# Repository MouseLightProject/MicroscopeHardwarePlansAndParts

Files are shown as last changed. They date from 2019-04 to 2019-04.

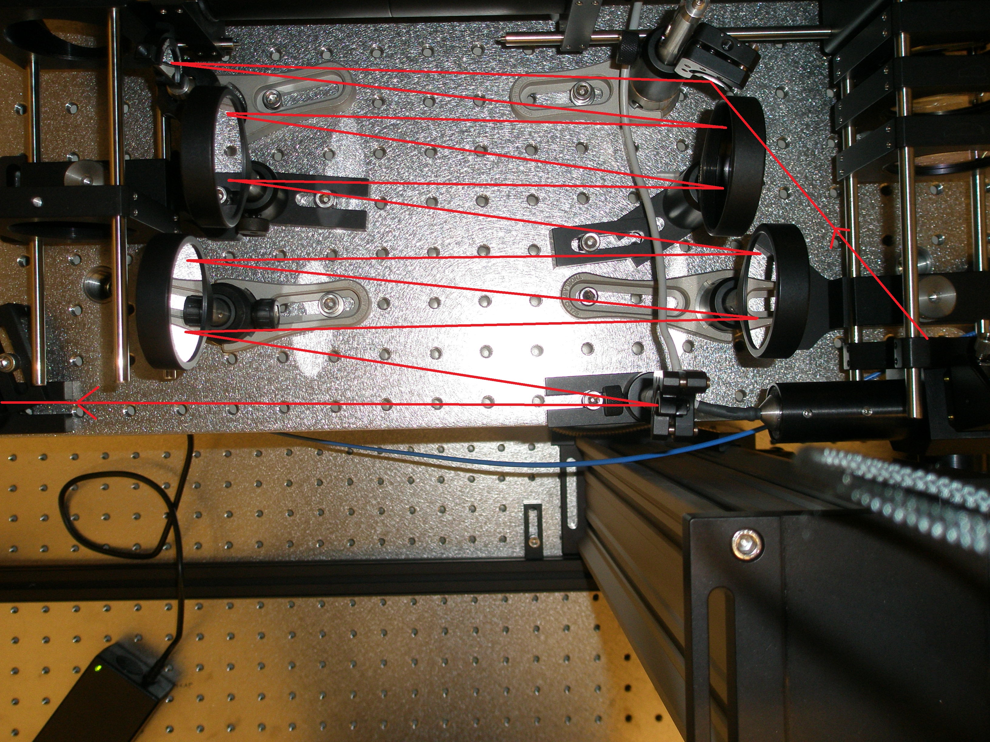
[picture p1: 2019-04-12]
Pictures/MouseBrainMicroscope_OpticalTriggerPic.JPG

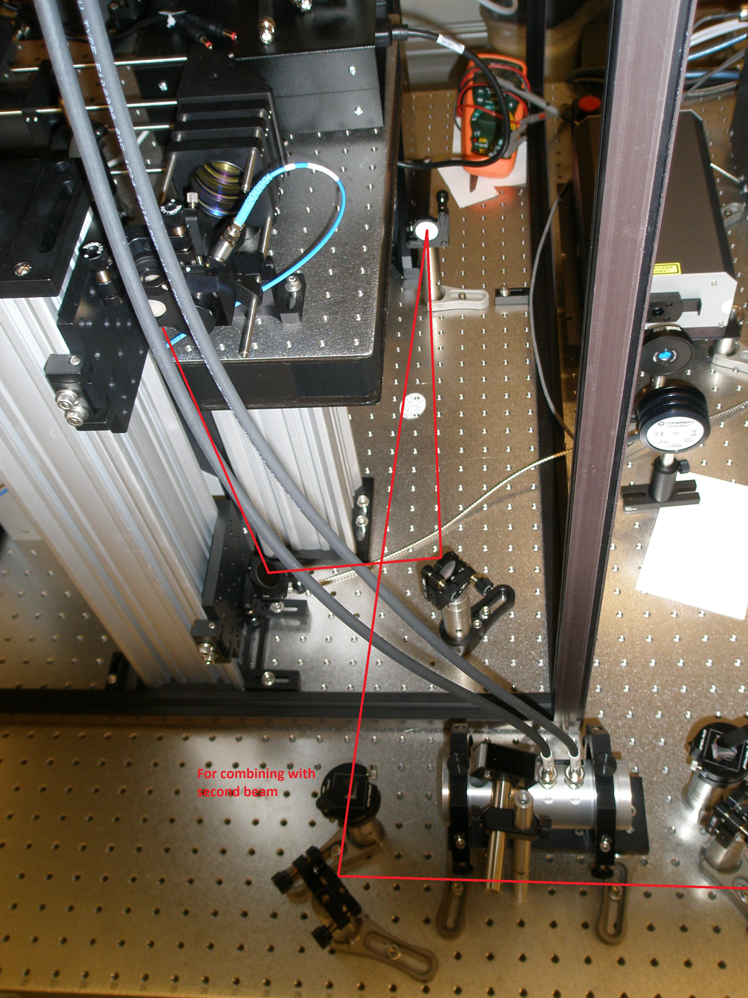
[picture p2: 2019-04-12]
Pictures/MouseBrainMicroscope_TableOpticsPic2.JPG

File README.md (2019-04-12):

# MouseLight Microscope Hardware

Hardware plans, component and assembly guide for the MouseLight microscope system described in [Economo et al., eLife, 2015](https://elifesciences.org/articles/10566)

## Contents
Please read the MouseLight_Microscope_AssemblyGuidelines for a rundown of the construction process and a table of content for the provided files and documentation.

## License
This project is licensed under the [Janelia Open-Source License](https://www.janelia.org/open-science/philosophy): see the LICENSE.md file for details

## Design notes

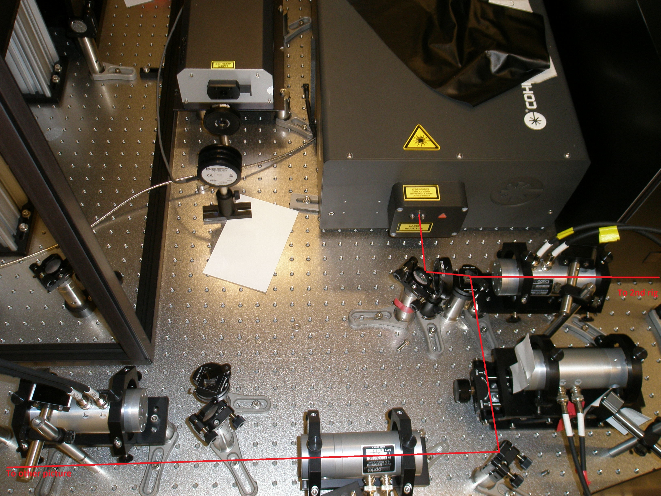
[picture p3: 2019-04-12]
Pictures/MouseBrainMicroscope_TableOpticsPic.JPG

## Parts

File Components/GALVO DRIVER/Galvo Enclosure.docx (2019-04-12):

Galvo Driver Enclsoure

Vault Folder: GALVOS

Nathan Clack

Research Specialist

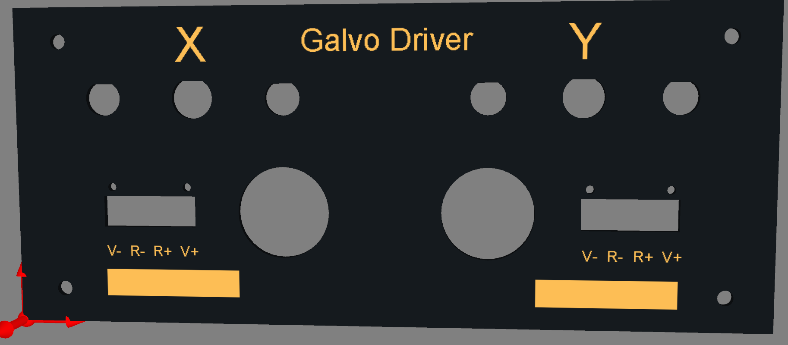
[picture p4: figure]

Steve Sawtelle
Electrical Engineer, ID&F
(571) 209-4158

# System Overview

The Galvo Driver Enclosure provides mounting, heat sink, and connectors for various Cambridge Technologies galvo drivers. One or two drivers can be mounted in the enclosure.

# Hardware Development

The Enclosure utilizes an off-the–shelf half-rack enclosure. The front panel can replaced by a custom front panel or the supplied panel can be modified to suit the particular need. The rear panel is replaced by a modular heat sink that provides various galvo mounting options. Wiring is highly dependent on the individual needs. The front panel design provides two BNCs and one Twin-Ax connectors for signal. A plug-able power supply connector is also provided for each channel. In addition a hole with grommet is provided for pass-through cables.

Materials

Qty | Value | Device | Manufacturer | Manufacturer PN | Digi-Key PN | Notes
1 | | Half-Rack Enclosure | Hammond | RMCV9038 | RMCV9038BK1-ND
1 | | Heat Sink | Aavid | 62725 | | Modified per drawing
1 | | Front Panel | Proto-Case | | | Custom design per drawing
2 | | Grommet | (McMaster-Carr) | 5269T65
2 | | BNC Male to Triax Female (3-Lug) | | | 1097-1008-ND | Adapt DAC output to Triac cable - shield isolated
4 | | BNC Bulkhead Jack, Panel Mount, Isolated | | | ACX1048-ND | For galvo monitor signals
2 | | Triax Jack, Bulkhead, 3 Lug | | | 501-1312-ND | For galvo command signals
2 | | 4 Position Terminal Block | | | 277-5751-ND | Panel mount for power
2 | | 4 Position Terminal Plug | | | 277-2432-ND | Wire to plug for power connector
AR | | Multiconductor Power Cable, 2 conductor, AWG 18, 250' spool | (Newark) | 62M3383 | | For power supply connection

# Assembly, Test, and Calibration

The galvo drivers should be lined up to the appropriate holes in the heat sink and attached with screws, with thermal grease between the heat sink and galvos.

The galvo drivers are wired up as required by the particular application.

Confidential Galvo Driver Enclosure

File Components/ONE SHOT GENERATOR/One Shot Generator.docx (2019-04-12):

One Shot Generator

Vault Folder: One-Shot Generator

Nathan Clack

Visiting Scientist

Magnus Karlsson
ID&F

# System Overview

This circuit creates an output pulse that happens exactly at the half-point of the input pulse with the possibility of some fine tuning using push-buttons. This eliminates manually setting a delay.

# Hardware Development

The circuit is made up of three parts:
1) An input detector (a comparator that compares the input to 3.3V/2)
2) An FPGA that
a) measures T = the length of time the output of the comparator is high (in units of 5 nS)
b) generates an output pulse T/2 ns after the output of the comparator goes high
3) Two push-buttons that allows an adjustment to the T/2 delay (in steps of +/- 5 nS) of the output

Schematic, Printed Circuit Board, BOM

See project file.

# Assembly, Test, and Calibration

No special requirements or notes.

Confidential One Shot Generator

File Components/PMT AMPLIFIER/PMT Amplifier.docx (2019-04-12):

PMT Amplifier

Karel Svoboda
Group Leader

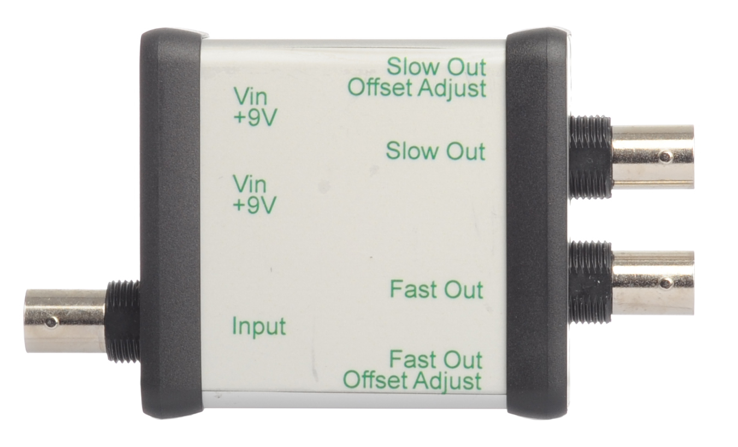
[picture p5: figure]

3/27/2012

Samantha Watkins
Engineering Specialist, ID&F
(571) 209-4371

# System Overview

The PMT Amplifier will be used as an error detector with microscope use. There will be fast and slow output. The fast output is the input signal from the PMT, but amplified with some filtering. The slow output will take the fast output and apply a low-pass filter with a 1 kHz roll off. The slow output will be an indicator of too long of a light exposure to the PMT, therefore the sensitive equipment, and will create a safety shutdown.

# Hardware Development

Materials

# Testing

The PMT Amplifier can be tested with a signal generator when RIN is replaced with a high value resistor. A PMT can also be used to test the Amplifier when a 0Ω resistor is used for RIN. The fast output should display a light pulse from the PMT and the slow output should give a low pass response when the PMT is exposed to too much light.

## Board Configurations

### R1: OPA657-OPA692-OP400

Stage 1: OPA657
Transimpedance Gain | 20 kΩ
Feedback Capacitor | 0.4 pF
Stage 2: OPA692
Gain | 2
Pulse Duration | 40 ns
Output Voltage Offset Adjust | Disabled. Pin grounded to allow for int. gain of 2
Stage 3: OP400
Gain | 1
Filter Cutoff – Freq Response | 1.6 kHz
Output Voltage Offset Adjust | Enabled

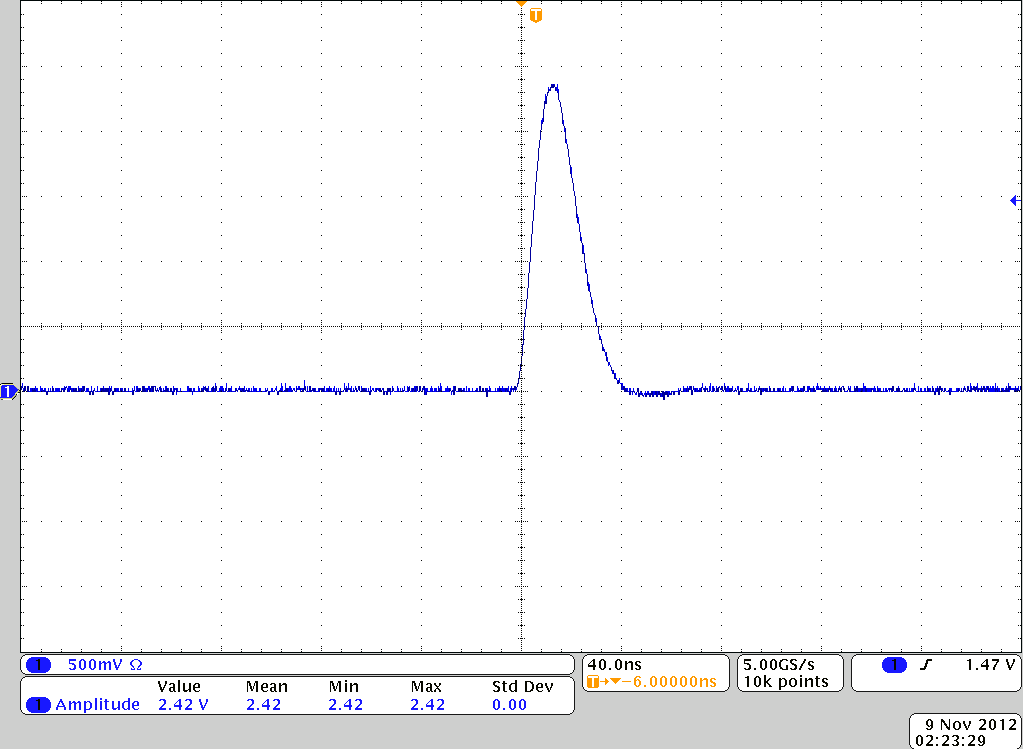
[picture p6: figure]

Fast Output from Stage 2: OPA657-OPA692-OP400

### R1: OPA657-AD810-OP400

Stage 1: OPA656
Transimpedance Gain | 100 kΩ
Feedback Capacitor | 0.5 pF
Stage 2: AD810
Gain | 2
Pulse Duration | 250 ns
Output Voltage Offset Adjust | Enabled
Stage 3: OP400
Gain | 1
Filter Cutoff – Freq Response | 1.6 kHz
Output Voltage Offset Adjust | Enabled

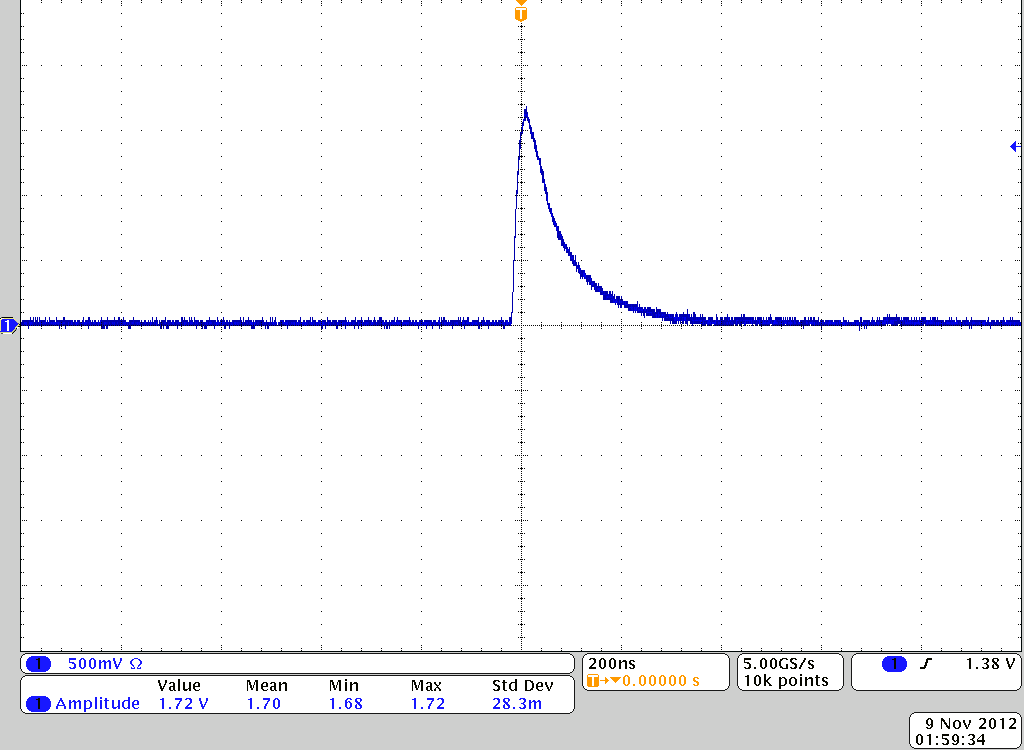
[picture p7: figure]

Fast Output from Stage 2: OPA657-AD810-OP400

### R1: OPA656-AD810-OP400

Stage 1: OPA656
Transimpedance Gain | 100 kΩ
Feedback Capacitor | 0.4 pF
Stage 2: AD810
Gain | 2
Pulse Duration | 180 ns
Output Voltage Offset Adjust | Enabled
Stage 3: OP400
Gain | 1
Filter Cutoff – Freq Response | 1.6 kHz
Output Voltage Offset Adjust | Enabled

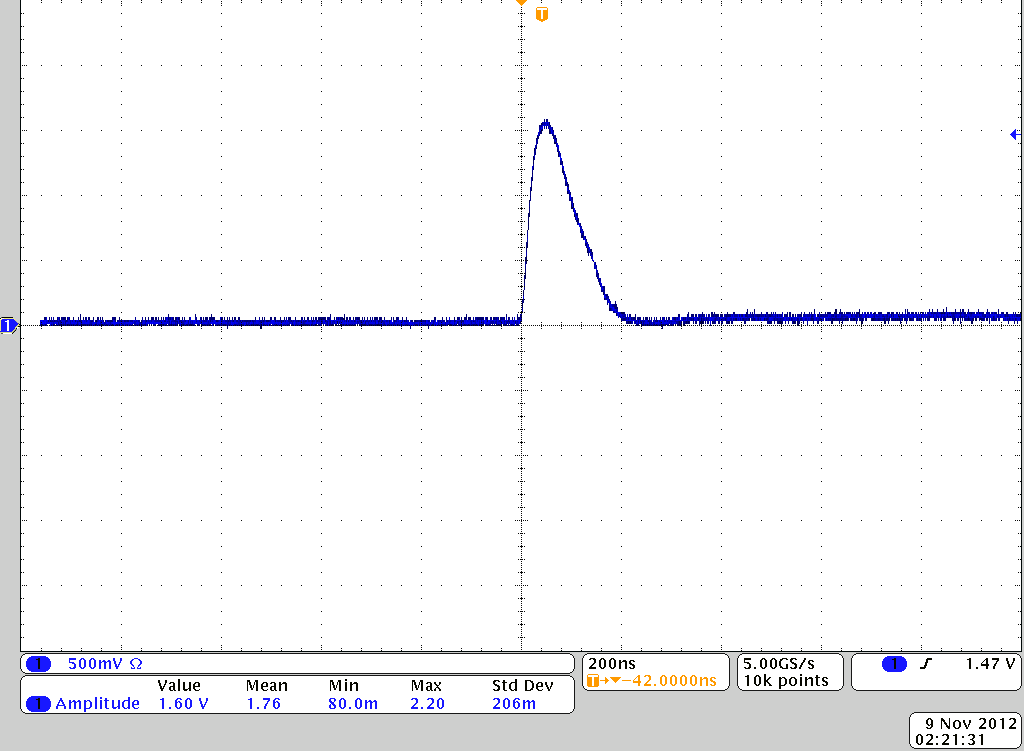
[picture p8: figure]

Fast Output from Stage 2: OPA656-AD810-OP400

### R1: OPA657-BUF634-OP400

Stage 1: OPA657
Transimpedance Gain | 100 kΩ
Feedback Capacitor | 0.4 pF
Stage 2: BUF634
Gain | 1
Pulse Duration | 320 ns
Output Voltage Offset Adjust | Disabled
Stage 3: OP400
Gain | 1
Filter Cutoff – Freq Response | 1.6 kHz
Output Voltage Offset Adjust | Disabled

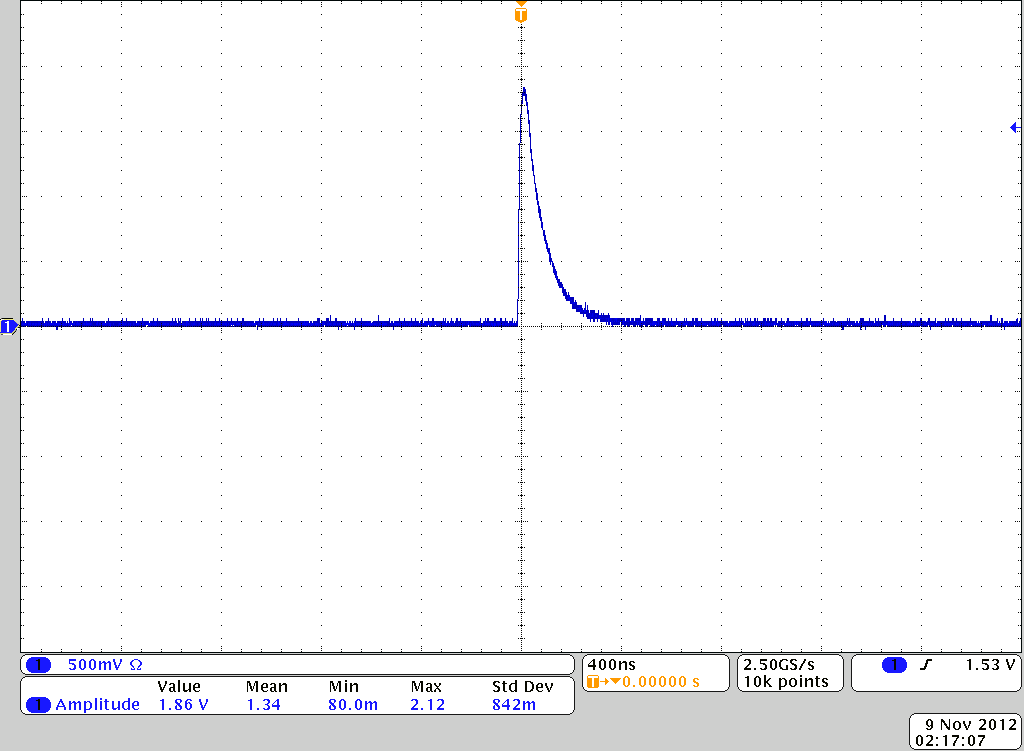
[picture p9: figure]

Fast Output from Stage 2: OPA657-BUF634-OP400

## Frequency and Gain Analysis

Freqin (@1V,20kΩ) | | Gain
| | OPA657 OPA692 | OPA657 AD810 | OPA656 AD810 | OPA657 BUF634
50kHz | 5.00E+04 | 7.4 | 5.72 | 5.76 | 6.4
100kHz | 1.00E+05 | 7.4 | 5.72 | 5.76 | 6.4
250kHz | 2.50E+05 | 7.4 | 5.72 | 5.76 | 6.4
500kHz | 5.00E+05 | 7.4 | 5.72 | 5.76 | 6.36
1MHz | 1.00E+06 | 7.36 | 5.56 | 5.64 | 6.36
2MHz | 2.00E+06 | 7.4 | 5.56 | 5.64 | 6.36
5MHz | 5.00E+06 | 7.4 | 5.2 | 5.32 | 6.36
10MHz | 1.00E+07 | 7.4 | 4.84 | 5 | 5.08
25MHz | 2.50E+07 | 7.2 | 3.32 | 3.64 | 2.2
50MHz | 5.00E+07 | 7.2 | 1.28 | 1.72 | 0.044
70MHz | 7.00E+07 | 6.8 | | 1.24 | 0.056
80MHz | 8.00E+07 | 6.4 | | 1
85MHz | 8.50E+07 | 6.1
90MHz | 9.00E+07 | 5.3
95MHz | 9.50E+07 | 4.8
100MHz | 1.00E+08 | 4.4
105MHz | 1.05E+08 | 3.96
110MHz | 1.10E+08 | 3.72

# Sample Circuit Set-Up

### R1: OPA656-AD810-OP400

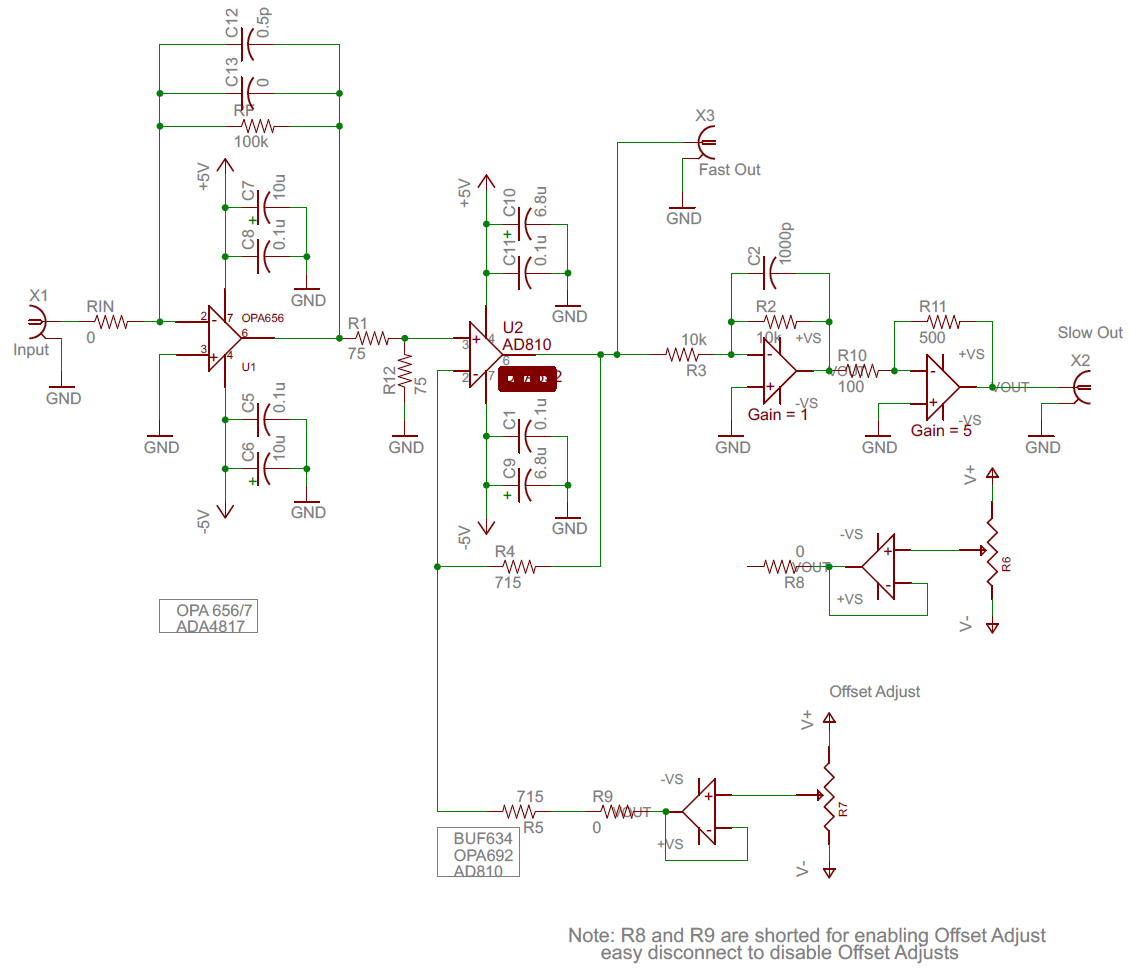
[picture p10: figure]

### R1: OPA657-BUF634-OP400

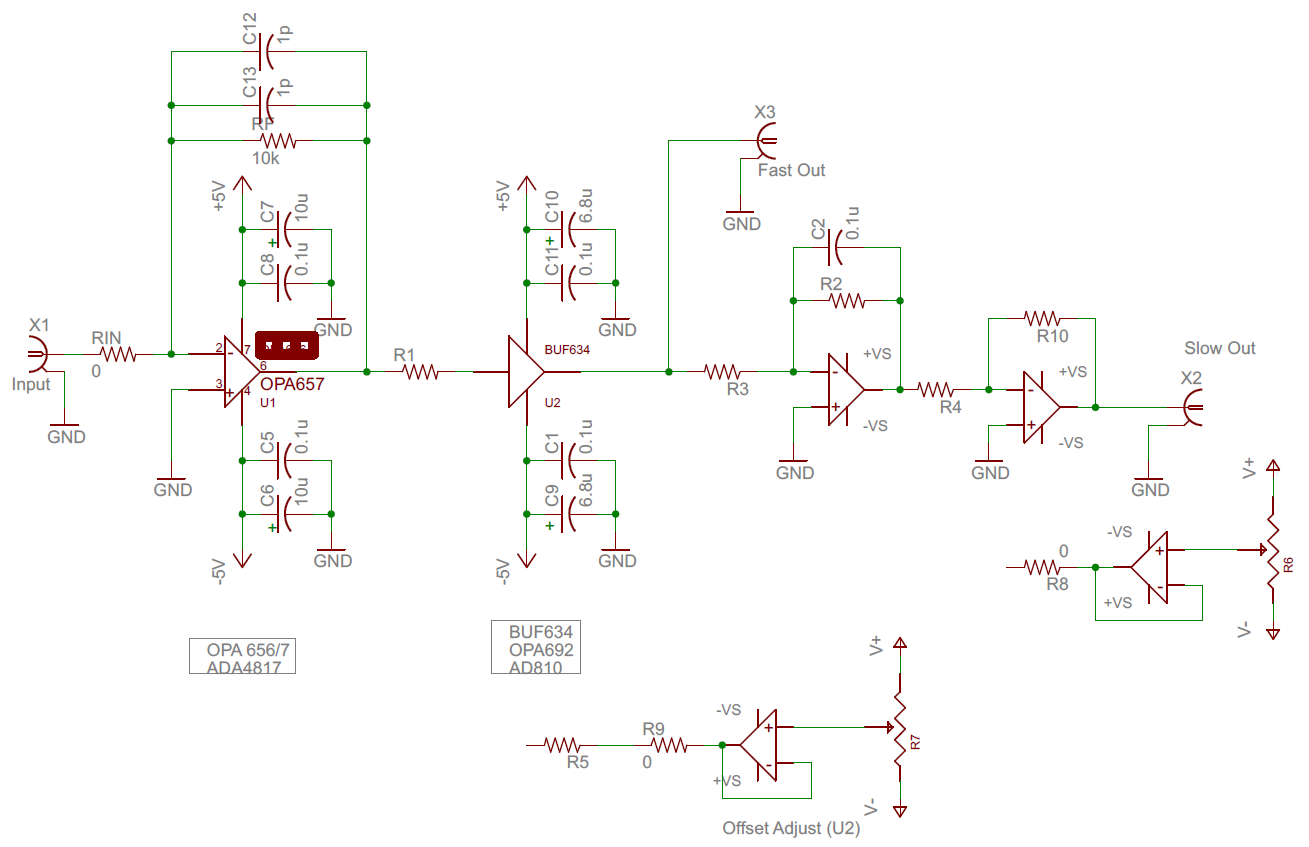
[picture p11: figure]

# Appendix

Assembly Note: R1 and Amp1 marked on the boards are the same, only differing in physical changes. Amp1 is the latest rendition in Vault as Revision B.


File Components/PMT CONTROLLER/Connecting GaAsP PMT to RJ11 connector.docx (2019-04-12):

Connecting GaAsP PMT to RJ11 connector.

The Hamamatsu H7422P-40MOD or H10770PB-40 SEL GaAsP PMTs terminate with bare wires. Connect the 4 power and control wires to a 4-6 (6 positions, 4 connectors, aka “RJ11”) modular plug a short distance from PMT. Attach a short piece of the appropriate 4 conductor cable to the connector with a crimper first, and then solder wires to wires.

Pinout:

PMT wire | PMT wire color | Connector pin
Vcc, +15V | Red | 4
GND | Black | 3
Vref | Blue | 2
Vcontrol | white | 1

Modular 6-4 (RJ11) connector pin assignment.


Pin 1

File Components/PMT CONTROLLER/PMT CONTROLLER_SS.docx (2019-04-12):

PMT CONTROLLER


The PMT Controller provides two channels of control for GaAsP Photo Multiplier Tubes. The low –noise design uses static logic, linear power supplies, and an AC line filters. The control voltages are independently adjustable over their entire range via a multi-turn control, with the voltages displayed on the built-in meters. Each PMT can be switched on and off independently. A trip circuit is built in to detect high PMT currents. Trip level and duration can be independently set for each channel. A trip condition turns off both PMTs and can be reset via a front panel control. External control of high voltage and trip reset are also provided.


Front Panel

- Trip Reset: resets a tripped condition
- LEDs: Power On, High Voltage On, Tripped
- Vctrl: Control Voltage Setting (each channel)
- PMT connector (each channel) Pin out (left to right):
  - 15V Supply Out
  - Ground
  - Reference Voltage In
  - Control Voltage Out
- PMT1 (2): Enable control for each PMT
- HV Ctl: High Voltage control: Normal or Override (Overrides trip)


Rear Panel

- AC inlet, power switch, fuse
- TTL HV CTL: External HV and trip control. Active high TTL, isolated) Pin out (left to right):
  - TTL Trip Reset In
  - TTL High Voltage Control In
  - Isolated Ground
  - 5V supply in for isolator
- PMT SIG: PMT pre-amp input for trip detect (each channel)
- Shield GND: Jumper to connect PMT SIG shield to local ground (each channel)
- Trip V: Adjust the trip detect level (monitor via test pin) (each channel)
- Trip Time: Adjust how long trip level must be active before trip (monitor via test pin) (each channel)
- GND: test point ground reference

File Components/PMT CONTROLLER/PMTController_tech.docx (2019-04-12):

PMT Controller

Vault Folder: PMT Controller

Nathan Clack

Research Specialist


Steve Sawtelle
Electrical Engineer, ID&F
(571) 209-4158

# System Overview

The PMT Controller provides two channels of control for GaAsP Photo Multiplier Tubes. The low –noise design uses static logic, linear power supplies, and an AC line filters. The control voltages are independently adjustable over their entire range via a multi-turn controls, with the voltages displayed on the built-in meters. Each PMT can be switched on and off independently. A trip circuit is built-in to detect high PMT currents. Trip level and duration can be independently set for each channel. A trip condition turns off both PMTs and can be reset via a front panel control. External control of high voltage and trip reset are also provided.

# Hardware Development

The PMT Controller is based off a previous Janelia design. Care was taken to eliminate switching noise. Only the panel meters use switching electronics.

The trip detect circuits have some high frequency noise filters (~30kHz), followed by a level comparator with adjustable threshold. This is followed by an adjustable trip delay circuit. Therefor a trip detect occurs when the input signal reaches a particular threshold and lasts a certain duration. The two trip signals are OR’ed together to create single trip event if either input satisfies the trip requirements. This in turn sets a latch to turn off the high voltage control and a trip indicator LED. The trip condition can be reset using the Trip Reset switch.

Each channel can be turned on and off independently. There is a common high voltage control.

Schematic


Printed Circuit Board


Materials

Qty | Value | Device | Manufacturer | Manuafcturer PN | Digi-Key PN | Designators
1 | 66010-004LF | RJ9 4P4C | FCI | 66010-004LF | 609-3785-ND | J1
2 | | HEADER 1X2 M RA | Molex | 22-12-2021 | WM2733-ND | JP1 JP2
1 | | HEADER 1X4 M ST | TE Connectivity | 3-644456-4 | A31114-ND | JP3
2 | | SWITCH-3PDT-VERT3PDT_VERT_RA | NKK | M2032S2A2W40 | 360-2858-ND | SW100 SW101
1 | | SWITCH-DPDT ON-NONE-ON | C&K | 7201P3CWAV2SE | CKN9728-ND | S1
1 | | SWITCH-SPDT ON-NONE-MOM | C&K | 7108P3CWAV2QE | CKN9716-ND | S100
5 | | TEST POINT | Keystone | 1045 | 1045K-ND | P1 P2 P3 P4 P5
11 | 0.1 | CAPS0805S | KEMET | C0805C104K1RACTU | 399-3486-1-ND | C5 C6 C7 C8 C12 C15 C16 C17 C18 C21 C22
2 | 0R-DNI | RESISTOR_SM0805S | DNI | DNI | DNI | R20 R21
2 | 5227161-9 | BNC, PCB , RA, LOW | TE Connectivity | 5227161-9 | A32261-ND | J2 J3
2 | 1K | RESISTOR_SM0805S | VISHAY | CRCW08051K00FKEA | 541-1.00KCCT-ND | R7 R9
2 | 1uF | CAPS0805S | Kemet | C0805C105KRACTU | 399-7409-1-ND | C3 C4
2 | 1uF/35V | CAPS0805S | MURATA | GRM31CR61H106KA12L | 490-5961-1-ND | C19 C20
8 | 2K | RESISTOR_SM0805S | VISHAY | CRCW08052K00FKEA | 541-2.00KCCT-ND | R5 R6 R16 R17 R18 R22 R26 R27
2 | 10K | POT3362M | Bourns | 3362M-1-103LF | 3362M-103LF-ND | R1 R4
4 | 10K | RESISTOR_SM0805S | VISHAY | CRCW080510K0FKEA | 541-10.0KCCT-ND | R11 R12 R13 R14
4 | 10uF/35V | CAPS1206S | TAIYO YUDEN | GMK316AB7106KL-TR | 587-3007-1-ND | C9 C10 C13 C14
2 | 16.9K | RESISTOR_SM0805S | VISHAY | CRCW080516K9FKEA | 541-16.9KCCT-ND | R23 R24
1 | 19E40 | ACOPIAN_PS | Acopian | 19E40 | from manufacturer | PS100
2 | 20K | POT3362M | Bourns | 3362M-1-203LF | 3362M-203LF-ND | R2 R3
3 | 20K | RESISTOR_SM0805S | VISHAY | CRCW080520K0FKEA | 541-20.0KCCT-ND | R15 R19 R25
1 | 47pF | CAPS0805S | JOHANSON | 500R15N470JV4T | 709-1175-1-ND | C11
2 | 50K | POT | Bourns | 3590P-4-503L | 3590P-4-503L-ND | R28 R29
1 | 74AHC1G02DBV | 74AHC1G02DBV | TI | SN74AHC1G02DBVR | 296-1088-1-nd | U3
1 | 74AHC1G08DBV | 74AHC1G08DBV | TI | SN74AHC1G08DBVR | 296-1091-1-ND | U8
2 | 100K | RESISTOR_SM0805S | VISHAY | CRCW0805100KFKEA | 541-100KCCT-ND | R8 R10
2 | 470pF | CAPS0805S - NPO | KEMET | C0805C471J5GACTU | 399-1133-2-ND | C1 C2
1 | 564-0200-132F | LED-TRI | DIALIGHT | 564-0200-132F | 350-1755-ND | D100
1 | 722RA | POWER_JACK_SHUNT | DNI | DNI | DNI | J4
1 | 74123D | IC MULTIVIBRATOR | NXP | 74HCT123D,653 | 568-9983-1-ND | U6
1 | 74279D | 74279D | TI | SN74LS279ADR | 296-29449-1-ND | U9
1 | ADG436 | ADG436 | ANALOG DEVICES | ADG436BRZ | ADG436BRZ | U10
1 | FOD0721 | OPTOCOUPLER | FAIRCHILD | FOD0721 | FOD0721-ND | U4
1 | 7019B-MTG | HEAT_SINK | AAVID | 7019B-MTG | 32-7019B-MT (MOUSER) | U$2
1 | LM340-5 | VREG_LM340_78X | TI | LM340T-5.0/NOPB | LM340T-5.0/NOPB-ND | U5
1 | LM340-15 | VREG_LM340_78X | TI | LM340T-15/NOPB | LM340T-15/NOPB-ND | U7
2 | FLEX CABLE/PCB | M12PTH | TE Connectivity | AFE12T/AF12/AFE12T | A9AAT-1202F-ND | JP4 JP5
2 | TLC3702 | COMPARATOR - DUAL | TI | TLC3702CDR | 296-1325-1-ND | U1 U2
1 | TS922 | OPAMP | ST MICRO | TS922IDT | 497-6035-1-ND | U11
2 | 5555979-1 | RJ11 6P4C | TE Connectivity | 5555979-1 | A31426-ND | J100 J101
2 | | HEADER-1X6-F | SAMTEC | SSQ-106-01-G-S | SAM1180-06-ND | ON DISPLAY BOARD
3 | | FERRITE- 0805-10uH | KEMET | L0805R100KPWST | 399-9588-1-ND | ON DISPLAY BOARD
1 | | DMM LED RED | MURATA | DMS-20PC-1-RS-C | 811-1001-ND | ON DISPLAY BOARD
1 | | DMM LED GRN | MURATA | DMS-20PC-1-GS-C | 811-1009-ND | ON DISPLAY BOARD
1 | | POWER ENTRY MODULE | DELTA | 06AR2D | 603-1132-ND | ON CHASSIS
3 | | CONN RECEPT FASTON 18-22AWG 250 | TE Connectivity | 696357-1 | 696357-1-ND | WIRED TO BOARD

# Assembly, Test, and Calibration

The PMT Controller is designed to require a minimum amount of wiring; most components mount directly to the main PCB.

PMT Controller Test Procedure

System Setup

1. PMT Controller
  a. Time trip potentiometer set to a minimum of 2ms
  b. Trip voltage potentiometer set to about 0.4V
    i. This can be measured using the test points; the center test point is ground
    ii. It can also be set by pointing the two dots on the potentiometer in the 9 o’clock position
    iii. This potentiometer ranges the trip voltage from about 0 - 4.6V
2. Pre-Amp – Stanford Research Systems SR570
  a. Make sure low noise is selected, 5µA/V, and invert are on/selected
  b. The filter, input offset, and bias voltage should all be off

Testing without the PMT

1. Using the 4 pin test cable check for noise in the power supply (J5, J6). Noise should be in the range of 5mV to 20mV peak to peak.
  a. This can be done by measuring between pins 1 and 2 of J5 and J6 with an AC Coupled channel.
2. The power supply for J5 and J6 should be at 15V.
3. Resistance across pins 2 and 3 of J5 and J6 should be 66kΩ with PMT Controller power turned off.
  a. It should not change when the potentiometer’s value is increased or decreased.

Testing with the PMT (p/n: ZD5760)


1. Make sure the PMT Controller is untripped before beginning the testing. Red LED should be off.
2. The LCD display should show a range from about 0 – 0.9V when the potentiometer is adjusted.
  a. This sets the gain for the PMT output pulse
3. Typically will not see anything on the oscilloscope with the gain less than 0.5V. Make sure the PMT pulse can be seen in the oscilloscope
4. Test trip by lowering the gain and blocking light from the PMT with your hand. Trip level should correspond with the trip voltage you set in the system setup section.

Confidential PMT Controller

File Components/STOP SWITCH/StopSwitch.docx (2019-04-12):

Stop Switch

Vault Folder: STOPSWITCH

Nathan Clack

Research Specialist


Steve Sawtelle
Electrical Engineer, ID&F
(571) 209-4158

# System Overview

The Stop Switch provides an emergency stop for stage drivers on a microscope. It consists of two parts: the stop switch in an enclosure and the interface electronics. The two are connected via a standard BNC cable.

# Hardware Development

The interface electronics is designed to be installed in-line with the existing cables so that no modifications are required.

The stop switch interface consists of OR’ing the stop line from each axis of the stage with the stop switch signal. The stop switch is a normally closed momentary switch. This ensures that any interruption, even a cut or missing cable will cause a STOP condition. Although any switch of this type can be used, a large prominent switch creates the best user interface.

Schematic


Printed Circuit Board


Materials

Partlist exported from C:/_Workspace/DATA/PROJECTS/STOPSWITCH/ECAD/StopSw_000333.sch at 8/29/2013 1:47:22 PM
| | | | Digi-Key | Manufacturer | Manufacturer PN
Qty | Value | Device | Designators
3 | | DB15 | J1 J2 J3 | A105027-ND | TE Connectivity | 3-106506-2
3 | | DB15DB15M | J4 J5 J6 | 5747841-6 | TE Connectivity | 5747841-6
4 | 0.1uF | CAPS0805S | C1 C2 C3 C4 | 478-3755-1-ND | AVX | 08053C104KAT2A
1 | 10K | RESISTOR_SM0805S | R1 | 541-10.0KCCT-ND | Vishay | CRCW080510K0FKEA
3 | 74AHC1G32DBV | 74AHC1G32DBV | IC1 IC2 IC3 | 296-1093-1-ND | TI | SN74AHC1G32DBVR
1 | 100 ohms | RESISTOR_SM0805S | R2 | 541-100CCT-ND | Vishay | CRCW0805100RFKEA
1 | BNC | 227161-9 | X1 | A32261-ND | TE Connectivity | 5227161-9
1 | | Enclosure (cut down) | | HM892-ND | Hammond | 1455J1601

STOP SWITCH - switch assembly
Quantity | Description | Manufacturer | PN | Source | Source PN | Notes
1 | Enclosure | Hammond | 1590AFLBK | Mouser | 546-1590AFLBK | Machine per picture
1 | Switch | | | McMaster | 5374T37
1 | BNC | Amphenol | 112624 | Mouser | 523-112624

# Assembly, Test, and Calibration


Wire the NC contact and common to the BNC connector.

Confidential Stop Switch

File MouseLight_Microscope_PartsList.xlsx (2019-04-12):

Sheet: BOM
Unit | Description | Part number | Rig qty | suggested spares | Qty to order | Item Cost | Rig cost | Rig unit subtotal | Spares cost | Spares Subtotal | Vendor | Old Quote # | Lead time | Comments | Inventor part file name | Column9 | Column10 | Column11 | Column12 | Column13 | Column14 | Column15 | Column16 | Column17 | Column18 | Column19 | Column20 | Column21 | Column22 | Column23 | Column24 | Column25 | Column26 | Column27 | Column28 | Column29 | Column30 | Column31 | Column32 | Column33 | Column34 | Column35 | Column36 | Column37 | Column38 | Column39 | Column40 | Column41 | Column42 | Column43 | Column44 | Column45 | Column46 | Column47 | Column48 | Column49 | Column50 | Column51 | Column52
Base and head movement | 2x1.5 ft custom size breadboard, research grade, with MicroLock | 04SI67446 | 1 | 0 | 1 | $1595 | $1595 | $2441.07 |  | $0 | Newport | 1054528 | 6 wk |  | Newport-04SI67446_Custom2x1p5ftBreadboard.ipt
Base and head movement | Elliptical mirror, 33 x 46.7 x 9.37mm, protected silver | 13E20ER.2 | 1 | 0 | 1 | $189 | $189 | $2441.07 |  | $0 | Newport |  |  |  | Newport_13E20ER.2_EllipSilverMirror.ipt
Base and head movement | Single Diameter Compression Tool for 1/32" Copper, Zinc-Plated Copper Sleeve | 3377T23 | 1 | 0 | 1 | $45.07 | $45.07 | $2441.07 |  | $0 | McMaster |  |  | Tool for fixing wire rope. Alternate methods of attaching head to cylinder are possible, but should be secure to avoid head dropping.
Base and head movement | Galvanized Steel Multipurpose Strand Rope, 1 x 7, 1/32" Diameter, 185 lb Break Strength, 50 ft. Length | 3498T41 | 1 | 0 | 1 | $1 | $1 | $2441.07 |  | $0 | McMaster |  |  | For attaching head to air cylinder
Base and head movement | Zinc-Plated Copper Oval Compression Sleeve for 1/32" Rope Diameter, 1/4" Sleeve Length, packs of 50 | 3898T29 | 1 | 0 | 1 | $1 | $1 | $2441.07 |  | $0 | McMaster |  |  | For attaching head to air cylinder
Base and head movement | Precision Thrd HI-Pressure Brass Pipe Fitting 1/8" Pipe Size, Tee, Fem X Male X Fem, 2900 PSI | 9171K860 | 1 | 0 | 1 | $16.73 | $16.73 | $2441.07 |  | $0 | McMaster-Carr |  |  |  | McMaster_9171K860_Tee.ipt
Base and head movement | Check valve, low cracking pressure, 1/8" NPT | AKB01B-N01S | 1 | 0 | 1 | $9.56 | $9.56 | $2441.07 |  | $0 | Allied Electronics/SMC | 1000238402 | 3 wk
Base and head movement | Metering valve w/ silencer, 1/8" NPT port | ASN2-N01-S | 1 | 0 | 1 | $4.24 | $4.24 | $2441.07 |  | $0 | Allied Electronics/SMC | 1000238402 | stock
Base and head movement | Aluminum shaft with DryLin S coating, OD 16mm, 254mm long. | AWM-16 | 2 | 0 | 2 | $14.86 | $29.72 | $2441.07 |  | $0 | IGUS | D475384REV0 | 1 wk |  | IGUS_16mmRod.ipt
Base and head movement | NC(D)G, High Speed/Precision Cylinder, Double Acting, Single Rod w/Options | NCGBN25-0500 | 1 | 0 | 1 | $28.86 | $28.86 | $2441.07 |  | $0 | Allied Electronics/SMC | 1000238402 | 3 wk |  | SMC_NCDGGN25-0500-U07US_Cylinder.iam
Base and head movement | Shock absorber, small | RBC0805 | 1 | 0 | 1 | $28.84 | $28.84 | $2441.07 |  | $0 | Allied Electronics/SMC | 1000238402 | 3 wk |  | SMC_RBC0805_ShockAbsorberSmall.ipt
Base and head movement | Pillow block, 16mm | RJUME-05-16 | 3 | 0 | 3 | $52.55 | $157.65 | $2441.07 |  | $0 | IGUS | D475384REV0 | 4-6 wk |  | IGUS_RJUME-05-16_PillowBlock16mm.iam
Base and head movement | 95mm structural rail, length .25 m | XT95-250 | 4 | 0 | 4 | $56.1 | $224.4 | $2441.07 |  | $0 | Thorlabs |  |  |  | Thor_XT95-250_95mmStructuralRail.ipt
Base and head movement | XT95 mounting plate | XT95P3 | 4 | 0 | 4 | $27.5 | $110 | $2441.07 |  | $0 | Thorlabs |  |  |  | Thor_XT95P3_XT95MountingPlate.ipt
Blocking slit hardware | Translating Post Holder, Min Height L1=2.38", Max Height L2=2.83" | PH2T | 1 | 0 | 1 | $54 | $54 | $146 |  | $0 | Thorlabs |  |  |  | PH2T_TranslatingPostHolderShort.iam
Blocking slit hardware | Center Mount 3" Post Joist | PJ301 | 3 | 0 | 3 | $16 | $48 | $146 |  | $0 | Thorlabs |  |  |  | PJ301_CenterMount3inPostJoist.ipt
Blocking slit hardware | Reaching 3" Post Joist | PJ302 | 1 | 0 | 1 | $15 | $15 | $146 |  | $0 | Thorlabs |  |  |  | PJ302_Reaching3inPostJoist.ipt
Blocking slit hardware | Universal post holder, height 1" | UPH1 | 1 | 0 | 1 | $29 | $29 | $146 |  | $0 | Thorlabs |  |  |  | Thor_UPH1_UnivPostHolder.ipt
Cage | Magnet tape | 5759K36 | 15 | 0 | 15 | $0.43 | $6.45 | $926.09 |  | $0 | McMaster-Carr |  |  | Feel free to use other, preferred methods for cage construction
Cage | Magnet tape, per foot, 1/16" thick, adhesive backed, strong pull | 5759K47 | 120 | 0 | 120 | $0.6 | $72 | $926.09 |  | $0 | McMaster-Carr |  |  | Feel free to use other, preferred methods for cage construction
Cage | Anodized Al sheet, 0.032 x 48.00 x 96.00 5005, Black anodize 2 stp class I | none | 2 | 0 | 2 | $110.72 | $221.44 | $926.09 |  | $0 | SAF.com |  |  | 4'x8' sheets need to be cut to size for cage with sheet metal shear. High freight charge is free for orders of 7 or more sheets
Cage | Construction cube | RM1G | 8 | 0 | 8 | $13.4 | $107.2 | $926.09 |  | $0 | Thorlabs |  |  | Feel free to use other, preferred methods for cage construction
Cage | Construction bracket | XE25A90 | 3 | 0 | 3 | $23.7 | $71.1 | $926.09 |  | $0 | Thorlabs |  |  | Feel free to use other, preferred methods for cage construction
Cage | Table clamp | XE25CL2 | 3 | 0 | 3 | $11 | $33 | $926.09 |  | $0 | Thorlabs |  |  | Feel free to use other, preferred methods for cage construction
Cage | Drop-In T-Nut, 1/4"-20 Tapped Hole, Qty: 10 | XE21T1 | 1 | 0 | 1 | $28 | $28 | $926.09 |  | $0 | Thorlabs |  |  | Feel free to use other, preferred methods for cage construction
Cage | 1/4"-20 Low-Profile Channel Screws (100 Screws/Box) | SH25LP38 | 1 | 0 | 1 | $21.6 | $21.6 | $926.09 |  | $0 | Thorlabs |  |  | Feel free to use other, preferred methods for cage construction
Cage | Construction rail, 30" long | XE25L30 | 4 | 0 | 4 | $24.5 | $98 | $926.09 |  | $0 | Thorlabs |  |  | Feel free to use other, preferred methods for cage construction
Cage | Construction rail, 36" long | XE25L36 | 3 | 0 | 3 | $27.5 | $82.5 | $926.09 |  | $0 | Thorlabs |  |  | Feel free to use other, preferred methods for cage construction
Cage | Construction rail, 48" long | XE25L48 | 4 | 0 | 4 | $34.7 | $138.8 | $926.09 |  | $0 | Thorlabs |  |  | Feel free to use other, preferred methods for cage construction
Cage | Blackout Fabric | BK5 | 1 | 0 | 1 | $46 | $46 | $926.09 |  | $0 | Thorlabs
Chromatic optics | IR stopping short pass filter | FF01-750/SP-30-D | 0 | 0 | 0 | $1200 | $0 | $1880 |  | $0 | Semrock |  | 1 Wk | Potentially helpful to stack with emission filters for IR blocking
Chromatic optics | Primary dichroic. | FF735-Di01-25x36 | 1 | 0 | 1 | $495 | $495 | $1880 |  | $0 | Semrock |  | 1 Wk
Chromatic optics | Secondary dichroic 35.5 x 50.2. Need to specify cutoff wavelength |  | 1 | 0 | 1 | $485 | $485 | $1880 |  | $0 | Semrock |  | 1 Wk | red/green secondary dichro. End user to specify filter coating. Need custom size: 35.5x50.2 mm. Easy to purchase custom size from Semrock.
Chromatic optics | Emission filter, channel 1, 30mm diam |  | 1 | 0 | 1 | $450 | $450 | $1880 |  | $0 | Semrock |  | 1 Wk | Emission filters need to have custom size 30mm diam. End user to specify filter coating. Easy to purchase custom size from Semrock. | EmissionFilter.ipt
Chromatic optics | Emission filter, channel 2, 30mm diam |  | 1 | 0 | 1 | $450 | $450 | $1880 |  | $0 | Semrock |  | 1 Wk | Emission filters need to have custom size 30mm diam. End user to specify filter coating. Easy to purchase custom size from Semrock.
Computer | Microsoft Visual Studio 2010 Professional w/MSDN | 2076506 | 1 | 0 | 1 | $591.51 | $591.51 | $4879.38 |  | $0 | CDW
Computer | Microsoft Windows 7 Professional SP1 64-bit | 2341134 | 1 | 0 | 1 | $141 | $141 | $4879.38 |  | $0 | CDW
Computer | Antec DF-85 Black Steel / Plastic ATX Full Tower Computer Case | N82E16811129087 | 1 | 0 | 1 | $139.99 | $139.99 | $4879.38 |  | $0 | Newegg |  |  | Exact match probably not necessary
Computer | StarTech Model TX3SPLIT12 12" TX3 Fan Power Splitter Cable | N82E16812200455 | 1 | 0 | 1 | $6.99 | $6.99 | $4879.38 |  | $0 | Newegg |  |  | Exact match probably not necessary
Computer | ASUS P9X79 WS LGA 2011 Intel X79 SATA 6Gb/s USB 3.0 SSI CEB Intel Motherboard with USB BIOS | N82E16813131798 | 1 | 0 | 1 | $379.99 | $379.99 | $4879.38 |  | $0 | Newegg |  |  | Exact match probably not necessary
Computer | EVGA 04G-P4-2690-KR GeForce GTX 690 4GB 512-bit GDDR5 PCI Express 3.0 x16 HDCP Ready SLI Support Video Card | N82E16814130781 | 1 | 0 | 1 | $999.99 | $999.99 | $4879.38 |  | $0 | Newegg |  |  | May not be available. Nvidia GTX 680 or better should be used.
Computer | StarTech PCI Express to 4 Slot PCI Expansion System Model PEX2PCI4 | N82E16815158247 | 0 | 0 | 0 | $426.99 | $0 | $4879.38 |  | $0 | Newegg |  |  | This part needed extensive mods to case to fit PI motor control cards. Probably best to order StarTech PEX2PCIE4L (listed separately), although this is untested
Computer | COOLER MASTER Silent Pro Gold Series RSC00-80GAD3-US 1200W ATX 12V v2.3 / EPS 12V v2.92 SLI Ready CrossFire Ready 80 PLUS GOLD Certified Modular Active PFC Power Supply | N82E16817171055 | 1 | 0 | 1 | $239.99 | $239.99 | $4879.38 |  | $0 | Newegg |  |  | Exact match probably not necessary
Computer | Intel Core i7-3930K Sandy Bridge-E 3.2GHz (3.8GHz Turbo) LGA 2011 130W Six-Core Desktop Processor BX80619i73930K | N82E16819116492 | 1 | 0 | 1 | $569.99 | $569.99 | $4879.38 |  | $0 | Newegg |  |  | Exact match probably not necessary
Computer | OCZ Vertex 4 VTX4-25SAT3-512G.M 2.5" 512GB SATA III MLC Internal Solid State Drive (SSD) | N82E16820227820 | 2 | 0 | 2 | $394.99 | $789.98 | $4879.38 |  | $0 | Newegg |  |  | Exact match probably not necessary
Computer | G.SKILL Ripjaws Z Series 64GB (8 x 8GB) 240-Pin DDR3 SDRAM DDR3 1600 (PC3 12800) Desktop Memory Model F3-12800CL10Q2-64GBZL | N82E16820231508 | 1 | 0 | 1 | $314.99 | $314.99 | $4879.38 |  | $0 | Newegg |  |  | Nathan Clack advises that 16 GB would be sufficient.
Computer | Rosewill Illuminated Mechanical Gaming Keyboard RK-9100BR with Cherry MX Brown Switch - Retail | N82E16823201053 | 1 | 0 | 1 | $129.99 | $129.99 | $4879.38 |  | $0 | Newegg |  |  | Exact match not necessary
Computer | Microsoft Basic Optical Mouse - Black | N82E16826105167 | 1 | 0 | 1 | $14.99 | $14.99 | $4879.38 |  | $0 | Newegg |  |  | Exact match not necessary
Computer | LITE-ON Black SATA DVD-ROM Drive Model iHDS118-04 | N82E16827106276 | 1 | 0 | 1 | $19.99 | $19.99 | $4879.38 |  | $0 | Newegg |  |  | Exact match not necessary
Computer | CORSAIR H100 (CWCH100) Extreme Performance Liquid CPU Cooler | N82E16835181017 | 1 | 0 | 1 | $114.99 | $114.99 | $4879.38 |  | $0 | Newegg |  |  | Exact match not necessary
Computer | PCI Express to 2 PCI & 2 PCIe Expansion Enclosure System - Full Length | PEX2PCIE4L | 1 | 0 | 1 | $425 | $425 | $4879.38 |  | $0 | StarTech.com |  |  | This part should work, as replacement for NewEgg N82E16815158247, but it is currently untested.
Custom mech parts | Holder for GSI 8kHz resonant mirror scanner on 30mm cage system, sealed. | J001061 | 1 | 0 | 1 | $1568 | $1568 | $14371 |  | $1852 | Zera Development |  | 5 wk |  | ResMirrorHolder_Sealed.ipt
Custom mech parts | Spacer for PIFOC mount bracket, needed for fast volume imager rig. | J001078 | 1 | 0 | 1 | $43 | $43 | $14371 |  | $1852 | Zera Development |  | 5 wk |  | SpacerForPIFOCHolderForFastVolImRig.ipt
Custom mech parts | Holder for Zeiss Axio Imager scan lens | J001160 | 1 | 0 | 1 | $270 | $270 | $14371 |  | $1852 | Zera Development |  | 5 wk |  | HolderForZeissAxioImagerScanLens.ipt
Custom mech parts | Riser piece for table-side base of head movement assembly | J001166 | 1 | 0 | 1 | $1060 | $1060 | $14371 |  | $1852 | Zera Development |  | 5 wk |  | HeadMovement_TableSideRiser.ipt
Custom mech parts | Holder for large spherical lens in det arm | J001167 | 1 | 0 | 1 | $443 | $443 | $14371 |  | $1852 | Zera Development |  | 5 wk |  | DetPath_LensHolder_ForPIFOCMountFromTopOnAutoSlicerRig.ipt
Custom mech parts | 30 mm to 60 mm Cage Plate Adapter, modified for clearance for mirr position meas beam | J001173 | 1 | 0 | 1 | $127 | $127 | $14371 |  | $1852 | Zera Development |  | 5 wk |  | LCP02_30mmTo60mmCagePlateAdapter_ModForMsrmntBeam.ipt
Custom mech parts | Adapter frame for using Semrock std thickness dichroics in std MIMMS emission splitting dichroic cube. Dichroic still needs to be custom large length x width. | J001179 | 1 | 2 | 3 | $50 | $50 | $14371 | $100 | $1852 |  |  | 1 wk | Not strictly necessary. Will keep 1mm thick (Semrock std thickness) emission splitting dichroic from rattling around. Easiest to have 3d printed. | AdapterForSemrockEmissSplitDichro.ipt
Custom mech parts | XT95 mounting plate, MOD with 1/4-20 hole for mounting to table. | J001203 | 4 | 0 | 4 | $27.5 | $110 | $14371 |  | $1852 | Zera Development |  | 5 wk |  | Thor_XT95P3_XT95MountingPlate_ModForAttachingToTable.ipt
Custom mech parts | Mount for Cambridge 6215H galvo scanning mirror on Thor LC6W cage cube. | JF-GM-AA0001 | 1 | 0 | 1 | $456 | $456 | $14371 |  | $1852 | Zera Development |  | 5 wk |  | Cambridge6215GalvoMountOnThorLC6WCube.ipt
Custom mech parts | Table-side baseplate for head movement assembly | JF-GM-AA0005 | 1 | 0 | 1 | $715 | $715 | $14371 |  | $1852 | Zera Development |  | 5 wk |  | HeadMovement_BasePlate.ipt
Custom mech parts | Brace piece for table-side of head movement assembly | JF-GM-AA0006 | 2 | 0 | 2 | $140 | $280 | $14371 |  | $1852 | Zera Development |  | 5 wk |  | HeadMovement_Brace.ipt
Custom mech parts | Rest for microscope head in upper position | JF-GM-AA0008 | 1 | 0 | 1 | $182 | $182 | $14371 |  | $1852 | Zera Development |  | 5 wk |  | HeadMovement_StopRiser.ipt
Custom mech parts | Holder for lower ball contacts for head-side head movement assembly | JF-GM-AA0009 | 2 | 0 | 2 | $180 | $360 | $14371 |  | $1852 | Zera Development |  | 5 wk |  | HeadMovement_BallHolder.ipt
Custom mech parts | Head-side baseplate of head movement assembly | JF-GM-AA0010A | 1 | 0 | 1 | $2125 | $2125 | $14371 |  | $1852 | Zera Development |  | 5 wk |  | HeadMovement_HeadSideBaseMount.ipt
Custom mech parts | Mount piece for 180 deg turn compression latch | JF-GM-AA0011 | 1 | 0 | 1 | $185 | $185 | $14371 |  | $1852 | Zera Development |  | 5 wk |  | HeadMovement_LatchHolder.ipt
Custom mech parts | Main mount plate for detection arm, with coarse z-movement (no z-stage) | JF-GM-AA0012A | 1 | 0 | 1 | $276 | $276 | $14371 |  | $1852 | Zera Development |  | 5 wk |  | DetPath_MountPlate_NoZStage.ipt
Custom mech parts | Holder for generic relay mirror from Zeiss tube lens to objective | JF-GM-AA0013 | 1 | 0 | 1 | $1000 | $1000 | $14371 |  | $1852 | Zera Development |  | 5 wk | Price guess | TubeLensToObjectiveMirrorHolder.ipt
Custom mech parts | Holder bracket for primary dichroic slider, with spring plunger for stop | JF-GM-AA0014 | 1 | 0 | 1 | $182 | $182 | $14371 |  | $1852 | Zera Development |  | 5 wk |  | DichroSliderHolderBracket_NoMotor.ipt
Custom mech parts | Custom cam for latch, Southco E3-41-15 (McMaster 1337A31) | JF-GM-AA0016 | 1 | 0 | 1 | $90 | $90 | $14371 |  | $1852 | Zera Development |  | 5 wk |  | CustomCamForCompLatch.ipt
Custom mech parts | Holder for secondary (emission splitting) dichroic, bottom half | JF-SV-AF0009B | 1 | 1 | 2 | $443 | $443 | $14371 | $443 | $1852 | Zera Development |  | 5 wk | Order spares for "hot-swapping" emission splitting dichroics | DetPath_DichroCubeBottom.ipt
Custom mech parts | Holder for secondary (emission splitting) dichroic, top half | JF-SV-AF0010A | 1 | 1 | 2 | $358 | $358 | $14371 | $358 | $1852 | Zera Development |  | 5 wk | Order spares for "hot-swapping" emission splitting dichroics | DetPath_DichroCubeTop.ipt
Custom mech parts | Thin holder for det arm beam tube end | JF-SV-AF0011 | 1 | 0 | 1 | $150 | $150 | $14371 |  | $1852 | Zera Development |  | 5 wk |  | DetPath_DichroCubeTubeHolder.ipt
Custom mech parts | Mounting plate for det arm upper assembly | JF-SV-AF0012B | 1 | 0 | 1 | $157 | $157 | $14371 |  | $1852 | Zera Development |  | 5 wk |  | DetPath_LensFilterMountPlate.ipt
Custom mech parts | Holder for emission filters | JF-SV-AF0013B | 2 | 2 | 4 | $186 | $372 | $14371 | $372 | $1852 | Zera Development |  | 5 wk | Order spares for "hot-swapping" emission filters | DetPath_EmissionFilterHolder.ipt
Custom mech parts | Mount plate for H7422 PMT (with intermediate shims) | JF-SV-AF0014 | 2 | 0 | 2 | $91 | $182 | $14371 |  | $1852 | Zera Development |  | 5 wk |  | DetPath_RectangPMTMountPlate.ipt
Custom mech parts | Shim for adjusting H7422 PMT z-position | JF-SV-AF0016A | 4 | 4 | 8 | $55 | $220 | $14371 | $220 | $1852 | Zera Development |  | 5 wk | Order spares in case PMT focus needs to be changed | SquarePMTShim_RevA.ipt
Custom mech parts | Holder for large elliptical mirror in det arm | JF-SV-AF0017 | 1 | 0 | 1 | $375 | $375 | $14371 |  | $1852 | Zera Development |  | 5 wk |  | DetPath_MirrorHolderDan3.ipt
Custom mech parts | Wall for det arm large mirror holder, back side | JF-SV-AF0019 | 1 | 0 | 1 | $370 | $370 | $14371 |  | $1852 | Zera Development |  | 5 wk |  | DetPath_MirrorHolderWall.ipt
Custom mech parts | Wall for large mirror holder, near side, with slot for adding large emission filter. | JF-SV-AF0021A | 1 | 0 | 1 | $300 | $300 | $14371 |  | $1852 | Zera Development |  | 5 wk |  | DetPath_MirrorHolderWall_NearSide.ipt
Custom mech parts | Holder for aspheric condenser lens in DOM det arm | JF-SV-AF0022 | 2 | 0 | 2 | $186 | $372 | $14371 |  | $1852 | Zera Development |  | 5 wk |  | DetPath_AshpereLensHolder.ipt
Custom mech parts | Intermediate sliding mounting plate for H7422 PMT | JF-SV-AF0023 | 2 | 0 | 2 | $95 | $190 | $14371 |  | $1852 | Zera Development |  | 5 wk |  | DetPath_RectPMTSliderPlate.ipt
Custom mech parts | Mounting bracket for primary dichro slider assembly | JF-SV-AF0025 | 1 | 0 | 1 | $109 | $109 | $14371 |  | $1852 | Zera Development |  | 5 wk |  | DetPath_DichroSliderBracket_STMotor.ipt
Custom mech parts | Support for back of scan assembly. | JF-SV-AF0033A | 3 | 0 | 3 | $133 | $399 | $14371 |  | $1852 | Zera Development |  | 5 wk |  | ScanAssemblyBackSupport.ipt
Custom mech parts | Blank 60mm cage plate, mod for OD 45mm Scan Lens mounting | JF-SV-AF0038 | 1 | 0 | 1 | $85 | $85 | $14371 |  | $1852 | Zera Development |  | 5 wk |  | Thor_LCP03_Blank60mmCagePlate_MODForScanLens.ipt
Custom mech parts | Tube with slit for shading. (AF Optical part is no longer available). | JF-SV-AF0045 | 1 | 0 | 1 | $50 | $50 | $14371 |  | $1852 |  |  | 5 wk |  | AFOptical_T50-50_MODToMakeLargerTube.ipt
Custom mech parts | Primary dichroic holder, with reflected light trap | JF-SV-AF0047 | 1 | 0 | 1 | $358 | $358 | $14371 |  | $1852 | Zera Development |  | 5 wk |  | DetPath_PrimaryDichroHolder.ipt
Custom mech parts | Bracket for PIFOC on MIMMS det arm, part 1 | JF-XX-MI0022A | 1 | 1 | 2 | $262 | $262 | $14371 | $262 | $1852 | Zera Development |  | 5 wk |  | PiezoZ-ScanBracket.ipt
Custom mech parts | Bracket for PIFOC on MIMMS det arm, part 2 | JF-XX-MI0023 | 1 | 1 | 2 | $97 | $97 | $14371 | $97 | $1852 | Zera Development |  | 5 wk |  | PiezoZ-ScanBracket_Pt2.ipt
Detectors | Metal package, high QE (GaAsP) PMTs. SEL: QE 45% min. at 550nm and Dark counts 4000 cps MAX. @ 25 deg C | H10770PB-40 SEL | 2 | 2 | 4 | $4104 | $8208 | $8708 | $8208 | $8208 | Hamamatsu | QUO-02465-N4N3B3 | 7 mo! | Very important to order with QE selection. Order spares as desired. It will be possible to use any H10770PB-40 or H10770PA-40 PMT with this system. Also, parts have been designed to use R3896/R9110 PMTs as well. Contact Dan Flickinger for info about these alternate parts. | PMT_H7422P-40MOD.ipt
Detectors | 2 channel PMT controller |  | 1 | 0 | 1 | $500 | $500 | $8708 |  | $8208 | HHMI - JFRC: ID&F |  | 1-2 mo | Docs for this should be received separately from JFRC - ID&F (Steve Sawtelle).
Digitizers | NI SHC68-68-EPM cable, shielded. | 192061-02 | 2 | 0 | 2 | $139 | $278 | $18560 |  | $0 | NI
Digitizers | NI BNC-2090A, shielded rack-mount BNC connector block | 779556-01 | 2 | 0 | 2 | $439 | $878 | $18560 |  | $0 | NI
Digitizers | NI PCIe-6353, X Series Data Acquisition. | 781049-01 | 1 | 0 | 1 | $1449 | $1449 | $18560 |  | $0 | NI
Digitizers | 12 bit, 500 MS/s, 2 ch. 8-lane PCI Express Digitizer with 128 Meg dual-port memory and up to 1.4 GBs throughput | ATS9350-002-USD | 2 | 0 | 2 | $6995 | $13990 | $18560 |  | $0 | Alazar | AAAQ1292 | ??
Digitizers | Upgrade that allows external clocking on ATS9350 from 500 MHz down to 1 MHz | ATS9350-005-USD | 1 | 0 | 1 | $645 | $645 | $18560 |  | $0 | Alazar | AAAQ1292 ??
Digitizers | Mezzanine SyncBoard that allows four (4) ATS9350 cards to operate in Master/Slave mode | ATS9350-007-USD | 1 | 0 | 1 | $995 | $995 | $18560 |  | $0 | Alazar | AAAQ1292 ??
Digitizers | C/C++ and Visual BASIC SDK for ATS class digitizers |  | 1 | 0 | 1 | $325 | $325 | $18560 |  | $0 | Alazar | AAAQ1292 ??
DOM Det Arm | Small linear guide slider, stroke 30 mm, NDN2-40.30 | 570890868 | 1 | 0 | 1 | $334.22 | $334.22 | $758.68 |  | $126.36 | Schneeberger | HHMI_SST-111031-00 | 2 wk
DOM Det Arm | BG39, 1-2mm thk, non-im qual, 28mm diam | BG39_28MMDIAM | 1 | 0 | 1 | $50 | $50 | $758.68 |  | $126.36 | Chroma | MS04075 | 5 wk | Item description is integral part of part specification. | BG39Filter_28mmDiam.ipt
DOM Det Arm | Ashperic lens, f = 23mm (actually f = 27mm) | KPA034-C | 2 | 1 | 3 | $75 | $150 | $758.68 | $75 | $126.36 | Newport |  |  |  | LensNewport_KPA034-C.ipt
DOM Det Arm | Round metric captive panel screw, length 20 | M0103-SS | 1 | 1 | 2 | $2.56 | $2.56 | $758.68 | $2.56 | $126.36 | Mouser |  |  |  | RAF_M0103-SS_CaptiveScrewM3x21p5.ipt
DOM Det Arm | Big elliptical mirror 1.5" x 2.121", enhanced aluminum | NT32-134 | 1 | 0 | 1 | $84.5 | $84.5 | $758.68 |  | $126.36 | Edmund |  | ?? not in stock |  | MirrorModelEdmundG32-134.ipt
DOM Det Arm | Lens, f=100mm, diam = 50mm, VIS 0 coated, inked | NT49-284-INK | 1 | 0 | 1 | $113 | $113 | $758.68 |  | $126.36 | Edmund Optics |  |  |  | Edmund_NT49-284-INK_AcromatLensF100VIS0.iam
DOM Det Arm | SM30 Retaining ring. M30.5-0.5 threads probably | SM30RR | 2 | 4 | 6 | $12.2 | $24.4 | $758.68 | $48.8 | $126.36 | Thorlabs |  |  | Extras for placing between stacked emission filters | Thor_SM30RR_SM30RetainingRing.ipt
Electro-optic modulators | Pockels cell linear amplifier | 302 RM | 1 | 0 | 1 | $3650 | $3650 | $7600 |  | $0 | Conoptics | 110311493#2
Electro-optic modulators | IR Laser pockels cell | 350-80-02-BK | 1 | 0 | 1 | $3725 | $3725 | $7600 |  | $0 | Conoptics | 110311493#2 | 1 mo
Electro-optic modulators | Conoptics Mount Ring Set and Base Plate from model 101 | None given | 1 | 0 | 1 | $225 | $225 | $7600 |  | $0 | Conoptics | 110311493#2
General hardware. | Hex Nut | ANSI B 18.2.4.1 M - M4 x 0.7 | 1 |  |  |  | $0 | $0 |  | $0 |  |  |  |  | ANSI B 18.2.4.1 M - M4 x 0.7Style 1.ipt
General hardware. | Hex Nuts (Inch Series) Hex Jam Nut | ANSI B18.2.2 - 1/4 - 20 | 1 |  |  |  | $0 | $0 |  | $0 |  |  |  |  | ANSI B18.2.2 - 1_4 - 20(3).ipt
General hardware. | Plain Washer (Inch )Type A and B | ANSI B18.22.1 - 1/4 - narrow - Type B | 4 |  |  |  | $0 | $0 |  | $0 |  |  |  |  | ANSI B18.22.1 - 1_4 - narrow - Type B.ipt
General hardware. | Hexagon Socket Head Cap Screw | ANSI B18.3 - 1/4 - 20 UNC - 1 | 2 |  |  |  | $0 | $0 |  | $0 |  |  |  |  | 1_4-1-UNC.ipt
General hardware. | Hexagon Socket Head Cap Screw | ANSI B18.3 - 1/4 - 20 UNC - 1 1/2 | 1 |  |  |  | $0 | $0 |  | $0 |  |  |  |  | ANSI B18.3 - 1_4-20 UNC - 1.5(31).ipt
General hardware. | Hexagon Socket Head Cap Screw | ANSI B18.3 - 1/4 - 20 UNC - 5/8 HS HCS | 4 |  |  |  | $0 | $0 |  | $0 |  |  |  |  | ANSI B18.3 - 1_4-20 UNC - 0.625(31).ipt
General hardware. | Hexagon Socket Head Cap Screw | ANSI B18.3 - No. 3 - 48 UNC - 3/8 HS HCS | 4 |  |  |  | $0 | $0 |  | $0 |  |  |  |  | ANSI B18.3 - 3-48 UNC - 0.375(31).ipt
General hardware. | Hexagon Socket Head Cap Screw | ANSI B18.3 - No. 8 - 32 UNC - 3/8 HS HCS | 1 |  |  |  | $0 | $0 |  | $0 |  |  |  |  | ANSI B18.3 - 8-32 UNC - 0.375(31).ipt
General hardware. | Hexagon Socket Head Cap Screw | ANSI B18.3 - No. 8 - 32 UNC - 5/8 HS HCS | 1 |  |  |  | $0 | $0 |  | $0 |  |  |  |  | ANSI B18.3 - 8-32 UNC - 0.625(31).ipt
General hardware. | Hexagon Socket Head Cap Screw | ANSI B18.3 - No. 8 - 32 UNC - 9/16 | 2 |  |  |  | $0 | $0 |  | $0 |  |  |  |  | ANSI B18.3 - 8-32 UNC - 0.5625(31).ipt
General hardware. | Hexagon Socket Head Cap Screw | ANSI B18.3 - No. 8 - 32 UNC - 9/16 HS HCS | 4 |  |  |  | $0 | $0 |  | $0 |  |  |  |  | ANSI B18.3 - 8-32 UNC - 0.5625(31).ipt
General hardware. | Forged Socket Head Cap Screw - Metric | ANSI B18.3.1M - M2.5x0.45 x 6 | 2 |  |  |  | $0 | $0 |  | $0 |  |  |  |  | ANSI B18.3.1M - M2.5x0.45 x 6(1).ipt
General hardware. | Forged Socket Head Cap Screw - Metric | ANSI B18.3.1M - M3x0.5 x 12 | 8 |  |  |  | $0 | $0 |  | $0 |  |  |  |  | ANSI B18.3.1M - M3x0.5 x 12(1).ipt
General hardware. | Forged Socket Head Cap Screw - Metric | ANSI B18.3.1M - M3x0.5 x 16 | 8 |  |  |  | $0 | $0 |  | $0 |  |  |  |  | ANSI B18.3.1M - M3x0.5 x 16(1).ipt
General hardware. | Broached Socket Head Cap Screw - Metric | ANSI B18.3.1M - M4x0.7 x 12 | 3 |  |  |  | $0 | $0 |  | $0 |  |  |  |  | ANSI B18.3.1M - M4x0.7 x 12(2).ipt
General hardware. | Hex Machine Screw Nut | ANSI B18.6.3 - 10 - 32 | 2 |  |  |  | $0 | $0 |  | $0 |  |  |  |  | ANSI B18.6.3 - 10 - 32(2).ipt
General hardware. | Hex Machine Screw Nut | ANSI B18.6.3 - 8 - 32 | 4 |  |  |  | $0 | $0 |  | $0 |  |  |  |  | ANSI B18.6.3 - 8 - 32(2).ipt
General hardware. | Hexagon socket set screw with cup point | ISO 4029 - M2.5 x 4 | 1 |  |  |  | $0 | $0 |  | $0 |  |  |  |  | M2.5-4.ipt
General hardware. | Hexagon thin nuts (chamfered) - Product grades A and B | ISO 4035 - M2.5 | 1 |  |  |  | $0 | $0 |  | $0 |  |  |  |  | M2.5.ipt
General hardware. | Hexagon thin nuts (chamfered) - Product grades A and B | ISO 4035 - M3 | 1 |  |  |  | $0 | $0 |  | $0 |  |  |  |  | M3.ipt
General hardware. | Hexagon Socket Head Cap Screw | ISO 4762 - M2 x 4 | 6 |  |  |  | $0 | $0 |  | $0 |  |  |  |  | M2-4.ipt
General hardware. | Hexagon Socket Head Cap Screw | ISO 4762 - M2.5 x 8 | 1 |  |  |  | $0 | $0 |  | $0 |  |  |  |  | M2.5-8.ipt
General hardware. | Hexagon Socket Head Cap Screw | ISO 4762 - M3 x 10 | 3 |  |  |  | $0 | $0 |  | $0 |  |  |  |  | M3-10.ipt
General hardware. | Hexagon Socket Head Cap Screw | ISO 4762 - M3 x 6 | 1 |  |  |  | $0 | $0 |  | $0 |  |  |  |  | ISO 4762 - M3 x 6ISO.ipt
General hardware. | Hexagon Socket Head Cap Screw | ISO 4762 - M4 x 8 | 1 |  |  |  | $0 | $0 |  | $0 |  |  |  |  | ISO 4762 - M4 x 8ISO.ipt
Hardware, could be categorized | 180 deg turn compression cam latch. Southco part# E3-41-15 | 1337A31 | 1 | 0 | 1 | $20.35 | $20.35 | $441.35 |  | $515.76 | McMaster-Carr |  |  |  | McMaster_1337A31_180degCompressionLatch.iam
Hardware, could be categorized | Santoprene foam rubber cord, cut to length | 6322K12 | 1 | 0 | 1 | $0.38 |  | $441.35 |  | $515.76 | McMaster-Carr
Hardware, could be categorized | SS spring plunger, 10-32, no lock nose, w/o thread lock | 84935A260 | 1 | 0 | 1 | $10.33 | $10.33 | $441.35 |  | $515.76 | McMaster-Carr |  |  |  | McMaster_84935A260_SpringPlunger.ipt
Hardware, could be categorized | Short Length SS Long-Nose Spring Plunger 5/8"-11 Thread, 7-50 lb Nose Force | 84985A91 | 1 | 0 | 1 | $7.85 | $7.85 | $441.35 |  | $515.76 | McMaster-Carr |  |  |  | McMaster_84985A91_MediumSpringPlunger.ipt
Hardware, could be categorized | Dowel pin, steel, 3/8 x 1/2 in, sold in 10 packs | 90145A619 | 6 | 4 | 10 | $0.79 | $4.74 | $441.35 | $3.16 | $515.76 | McMaster-Carr |  |  |  | McMaster_90145A619_DowelPin.ipt
Hardware, could be categorized | 18-8 SS wire lockable socket head cap screw 10-32 x 0.5" | 90152A255 | 1 | 1 | 2 | $1 | $1 | $441.35 | $1 | $515.76 | McMaster-Carr |  |  |  | McMaster_90152A255_ScrewWHoleShort.ipt
Hardware, could be categorized | 18-8 SS wire lockable socket head cap screw 10-32 x 1" | 90152A261 | 1 | 1 | 2 | $1 | $1 | $441.35 | $1 | $515.76 | McMaster-Carr |  |  |  | McMaster_90152A261_ScrewWHoleLong.ipt
Hardware, could be categorized | Nylon Tip 18-8 SS Socket Set Screw 8-32 Thread, 1/8" Length | 90291A183 | 12 | 0 | 12 | $0.91 | $10.92 | $441.35 |  | $515.76 | MCMASTER |  |  |  | 90291A183_SS8-32NylonTipSetScrew.ipt
Hardware, could be categorized | Nylon Tip 18-8 SS Socket Set Screw 8-32 Thread, 3/16" Length | 90291A189 | 2 | 0 | 2 | $0.5 | $1 | $441.35 |  | $515.76 | McMaster-Carr |  |  |  | McMaster_90291A189_SS#8-32SetScrewNylonTip.ipt
Hardware, could be categorized | Metric 18-8 Stainless Steel Large-Diameter Flat Washer, M3 Screw Size, 9MM OD, .7MM-.9MM Thick, packs of 100 | 91116A120 | 8 | 0 | 8 | $0.02 | $0.16 | $441.35 |  | $515.76 | McMaster-Carr |  |  |  | McMaster_91116A120_M3WasherLargeDiameter.ipt
Hardware, could be categorized | Stainless steel dowel pin, 2mm diam, 8mm long | 91585A017 | 12 | 0 | 12 | $0.11 | $1.32 | $441.35 |  | $515.76 | McMaster-Carr |  |  |  | McMaster_91585A017_DowelPinM2.ipt
Hardware, could be categorized | Stainless steel wave washer, M3 | 92168A101 | 8 | 42 | 50 | $0.05 | $0.4 | $441.35 | $2.1 | $515.76 | MCMASTER |  |  |  | 92168A101_WaveWasherM3.ipt
Hardware, could be categorized | M2x8, Socket head cap screw, flat head, 90 deg taper, ss | 93395A176 | 1 | 1 | 2 | $0.56 | $0.56 | $441.35 | $0.56 | $515.76 | McMaster-Carr |  |  |  | McMaster_93395A176_FlatHeadScrew.ipt
Hardware, could be categorized | PVC Hex Nut 5/8"-11 | 94806A044 | 1 | 0 | 1 | $3 | $3 | $441.35 |  | $515.76 | McMaster |  |  |  | McMaster_94806A044_5-8-11HexNut.ipt
Hardware, could be categorized | Chrome plated balls, sold in pack of 100 | 9528K19 | 3 | 0 | 3 | $0.09 | $0.27 | $441.35 |  | $515.76 | McMaster-Carr |  |  |  | McMaster_9528K19_3-8inBall.ipt
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

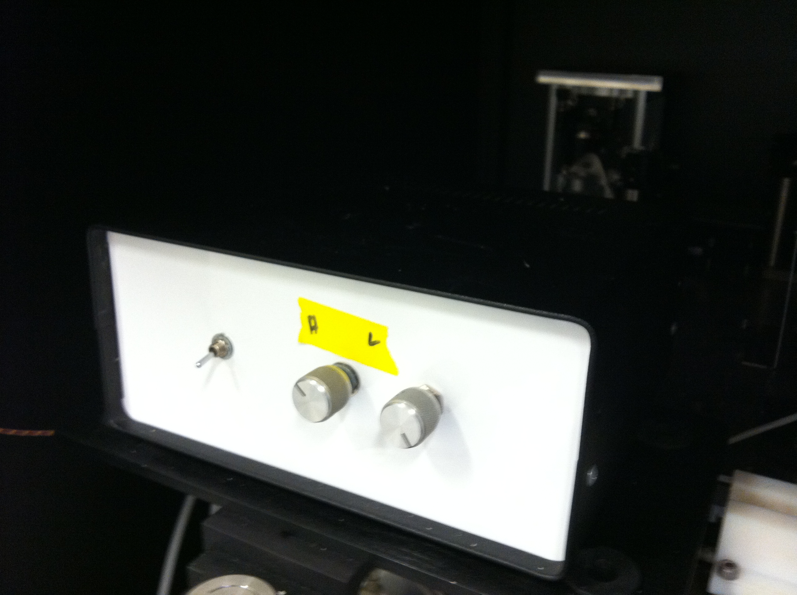
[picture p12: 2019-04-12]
Components/RESONANT MIRROR CONTROLLER/Resonant Mirror Controller.JPG

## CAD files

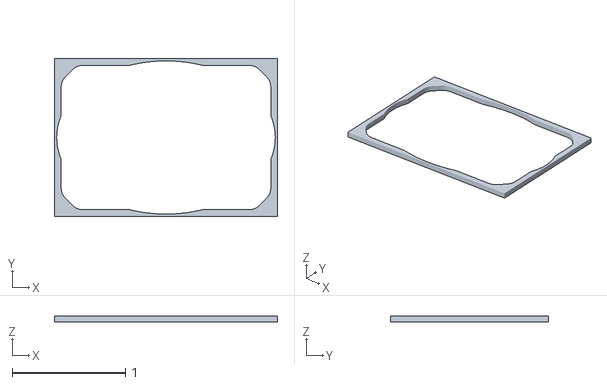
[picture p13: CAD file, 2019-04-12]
Fabrication Plans/J001179_hard_inch.stl
1.97 x 1.39 x 0.0551

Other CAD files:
Components/GALVO DRIVER/HEATSINK/Galvo Driver Heatsink.dwg
Components/GALVO DRIVER/HEATSINK/Heatsink.ipt

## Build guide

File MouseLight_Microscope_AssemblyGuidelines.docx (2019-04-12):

HHMI-JFRC

Daniel Flickinger

flickingerd@janelia.hhmi.org

12 April 2019

# Mouse Brain Microscope Assembly and Alignment Guidelines

# 1) Overview

This document is intended to provide guidelines for assembling and aligning the custom two-photon microscope designed for long-term whole mouse brain imaging at the Janelia Farm Research Campus by Nathan Clack, Karel Svoboda, and members of the JFRC Instrument Design and Fabrication department. It only covers the microscope itself, the table optics, and cage. The sample bath and stages, vibratome, and custom electronic assemblies will be covered in other documents. It is intended to provide useful information for someone who already has experience with building custom laser scanning microscopes, and will probably not allow others who lack this or similar experience to successfully build this microscope, unless they possess extensive optical and physical knowledge (and/or extensive free time). The following additional documents will be used for microscope construction:

            1. Parts list: MouseLight_Microscope_PartsList.xlsx
            2. 3D model: 3D Models/MouseLight_Microscope_Version_2.dwfx
            3. Part fabrication drawings: Fabrication Plans/
            a. Pictures:
            b. MouseBrainMicroscope_OpticalTriggerPic.JPG
            c. MouseBrainMicroscope_TableOpticsPic.JPG
            d. MouseBrainMicroscope_TableOpticsPic2.JPG

# 2) Document notes

## a) Parts list

This is a nearly full parts list for the whole microscope, table optics, and cage. Some spare parts are suggested to be bought. Notes are included with some items where there may be difficulty in ordering the exact correct thing, or when some thought will be necessary to determine what should be purchased. The “Table Optics” section is only approximately sufficient, as the required table optics are somewhat variable from one table to the next.

## b) 3D model

The 3d model DWFX file can be opened by the Autodesk Design Review (http://usa.autodesk.com/design-review/) software, which is free to download and install. This file contains a full 3D model. It contains metadata about each part, allows the visibility of each part to be controlled, and allows taking measurements between any model features.

## c) Part fabrication drawings

There is one drawing for each custom, mechanical part, which should be all that is necessary for manufacturing. Not all machine shops will be able to fabricate all of the parts, as some are a bit complicated. We have used Zera Development Company (Santa Clara, CA) extensively for nearly all of these parts, and have found them to provide a great value and relatively quick turnaround. Any included STL files are for parts that we have always had 3d printed. We have used Objet Connex 3d printers for these parts. Any rapid plastic prototying company using a similar (multi-jet/poly-jet) technology should be able to create functional parts using the STL files.

# 3) Guidelines for features not in 3D model

## a) Optics mounting (glue based)

All optics should be in the 3D model. The optics that don’t have an obvious retaining ring or set screw are mounted using glue. The only glue that has been used for this at Janelia is Hardman “Double Bubble Red” quick-setting epoxy, available from McMaster-Carr 7538A11. The following pictures show recommended locations for gluing (generally, small amounts like ~1x4mm beads along optics edges, or larger amounts for the larger optics). Certainly, other gluing methods could work, but mounts were designed for glues of a similar, thick viscosity. Less viscous glues would creep over clear apertures for many of these optics.

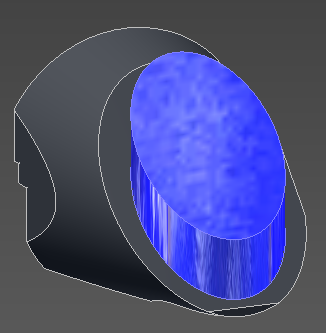
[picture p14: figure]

Figure 1. Large, elliptical mirror

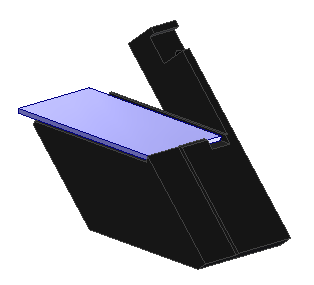
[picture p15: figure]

Figure 2. Primary dichroic

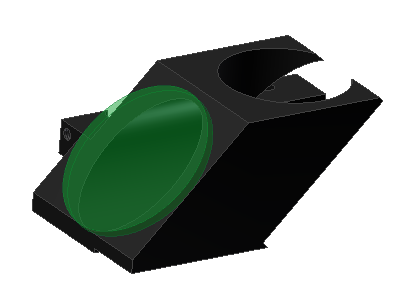
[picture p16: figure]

Figure 3. Light trap

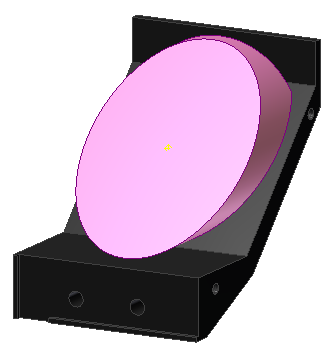
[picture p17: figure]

Figure 4. Large elliptical mirror in detection arm

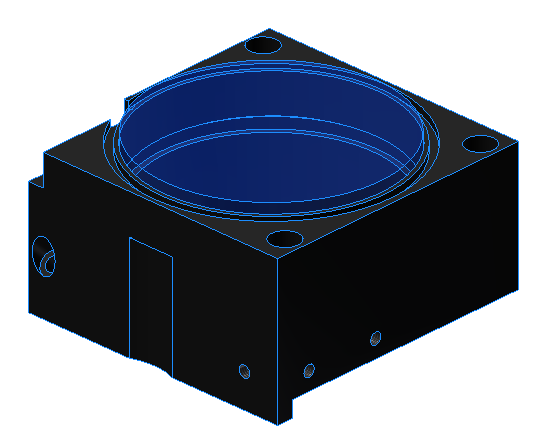
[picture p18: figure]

Figure 5. Large achromat

The secondary dichroic is not glued in place. It is held by three 002 buna-n o-rings, which are placed sideways in the three shallow slots in the top half of the dichroic cube.

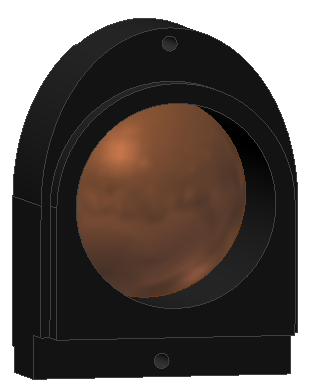
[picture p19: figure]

Figure 6. Aspheric lenses (Glue is carefully placed between walls and steeply inclined portion of lens, such that it doesn’t enter the used aperture of the convex lens surface)

## b) Connection of microscope head to pneumatic cylinder

The large pneumatic cylinder provides damping, such that if the microscope head is released at the top of its movement, it will settle slowly to the bottom, without doing damage to the optics. It was intended to be possible as well to attach controlled air to the cylinder, such that the head up and down movement could be automated (in which case it would also be necessary to design a new, automated head latch). To allow for the least amount of mechanical constraint, the microscope head is attached to the pneumatic cylinder with a wire rope that is threaded through the two socket head cap screws with drilled heads that are present in the model. The wire rope, compression sleeves, and crimping tool for this are included in the parts list.

## c) Cage construction

Nearly all materials for constructing a cage are included in the parts list. The cage size that we use is 38”w x 50”d x 32”h. The construction should be mostly self-explanatory. The construction angle brackets are used to strengthen the front of the cage against skew, as it doesn’t have a wall to provide this strength. The top, back, and sides are covered with black, anodized aluminum sheets that we custom cut from 4’x8’ sheets. We attach the walls with magnetic tape. Care must be taken when applying the magnetic tape. All surfaces should be cleaned first. Then, tape should be adhered to the frame, and a second set of tape should be magnetically attached to this tape. The adhesive should be removed from this tape, and each wall should be attached one at a time, adhering all of the second set of tape to each wall all at once. This is necessary because the magnetic tape has alternating N and S domains, and this method ensures that the all of the tape on each wall will align properly with all of the tape on the frame. (If the tape doesn’t align properly it will repel instead of attract!) The tape should further be burnished well on the frame and walls to ensure proper adhesion. The thinner tape in the parts list is for attaching to the front curtain.

## d) Gluing balls and rods for microscope head kinematic attachment to table

All 3 balls and 6 rods should have epoxy applied to where they touch the metal. We have used the Hardman Red quick-set epoxy for this (see gluing optics section), but it would be better to use a longer setting epoxy. After the epoxy is applied and all balls and rods have been placed, but well before the epoxy sets, the head should be attached to the base and the latch secured. In this way, the force from the latch will force each ball and rod into its pocket, reducing the glue thickness between each of these elements and the pocket walls.

## e) Optical trigger optics

The optical trigger optics are pictured in MouseBrainMicroscope_OpticalTriggerPic.JPG, with an approximate beam path. These are located on the raised optical table. The resonant mirror is the source of the alignment beam (ultimately coming from the fiber coupled 635nm laser source), at the lower right of the image. Not pictured is the photodiode detector, located just outside the lower left side of the image. The optics need to be aligned such that the alignment beam hits the photodiode at the end (turnaround) of the scan line, at the intended imaging resonant scan amplitude (usually full amplitude). The length of the propagation line is set roughly by the Rayleigh range of the beam after the fiber collimator. This is because the precision of the triggering can be increased by lengthening the propagation line, up until the propagation length roughly exceeds the Rayleigh range. At that length, any further increase in the propagation length comes along with a proportional increase in the beam size, resulting in no further triggering precision. Sufficient triggering precision is probably achievable with a shorter propagation line, but this has not been experimentally confirmed.

## f) Table optics and periscope

The table optics and periscope are pictured in MouseBrainMicroscope_TableOpticsPic.JPG and MouseBrainMicroscope_TableOpticsPic2.JPG . Note that the system pictured uses two lasers. The beamline for the main imaging laser (Coherent Chameleon) has been approximately drawn. The parts list only contains parts for this main imaging line, although it assumes that one laser will be split between two rigs, as illustrated in the picture. The order of optics as pictured is:

            1. Dielectric mirror (see note in parts list),
            2. Half-wave plate
            3. Polarizing beamsplitter cube
            4. Silver mirror
            5. Electro-optic modulator (Pockels cell) in crossed orientation
            6. (Switch to second picture) Silver Mirror
            7. Polarizing beamsplitter (for second beam line—not in parts list)
            8. Silver mirror (placed within reach of user for ease of aligning beam into microscope). This is the “main table optics alignment mirror” referred to in section 4)a)7.
            9. Silver mirror
            10. Periscope (two silver mirrors)
            11. 1/2” silver mirror for direction to resonant mirror (this part is contained in the 3D model).

The upper and lower mirror assemblies in the periscope are made using the same parts (these are hard to see in the picture). They each consist of a XT95P11 rail carriage, and a kinematic mirror mount with a H45 45deg mirror mount inserted. Note that all pictured mirror mounts are Thorlabs KM100 mounts, while it is recommended in the parts list to use Thorlabs Polaris-K1 mounts. These should hopefully reduce long-term beam wander, which is often observed.

It’s assumed that the user is familiar with setting up these optics and aligning the beam through them.

# 4) Adjustment of microscope optics

## a) Excitation optics

The following is intended to be a general outline of the procedure for adjusting/aligning the excitation optics of the microscope, and will lack step-by-step details. The general procedure is as follows (all accessory parts mentioned are contained in parts list):

            1. Set up all optics as in 3D model. Precise distances between all adjustable optics need not be met at this stage.
            2. Use periscope optics and adjustable mirror on resonant mirror assembly to center input beam on resonant mirror.
            3. Adjust resonant mirror angle (while mirror is off) to center beam on cage attached to res mirror assembly exit (use, e.g., Thorlabs LCPA1 for this).
            4. Adjust 2”, right-angle kinematic mount after res mirror assembly such that beam afterwards is aligned with cage
            5. Adjust separation of three lens set after res mirror from 3 lens set after 2” mirror such that beam is collimated at galvo mirror (Thorlabs SI100 is useful for this—laser must be set to “alignment mode” or otherwise set to CW operation for this to work). The distances between the three lenses in the first or second lens set are not critical.
            6. Adjust separation of res mirror assembly from first three lens set such that beam is stationary at position of galvo mirror when res mirror is oscillating.
            7. Beam should be centered on galvo mirror. If it is slightly off, then it should be centered with a slight tweak of the “main table optics alignment mirror”, which should have been set up as a faraway (beam-wise), yet accessible mirror on the main optical table (first mirror before periscope, if the table optics are set up as shown in the pictures). Using this mirror ensures minimal angular beam errors as the beam position is tweaked downstream. It will be used often for alignment.
            8. Use the “main table optics alignment mirror” (see step 7) and galvo mirror angle (while galvo mirror driver is on and centered at zero control volts) to align the beam with the cage after the galvo mirror. The Special Optics scan lens will need to be removed for this step.
            9. Replace Special Optics scan lens and adjust separation of this lens and Zeiss tube lens such that beam is collimated at objective (again, SI100 can be used for this).
            10. Adjust distance from galvo mirror to Special Optics scan lens until beam is stationary at objective back aperture when either res mirror or galvo mirror is scanned. Note that the entire assembly from the res mirror to the galvo mirror will need to be moved for this.
            11. Perform “Regular alignment procedure” outlined in section 5).

## b) Detection optics

First, take care to set the stop of the primary dichroic carriage properly, at the distance indicated in the 3d model. This stop is a long M3 set screw, which should be secured with a nut. After this, the only remaining adjustment in the detection optics is the PMT positions. The PMT z-positions is set by adding/removing shims, and the number of shims shown in the 3D model should be correct (as measured with an existing microscope). The PMT x,y-positions are best set while imaging. A bright, uniform fluorescence field should be imaged, such as a pool of fluorescein, or a plastic, fluorescent slide. The beam power should be increased and the PMT gain should be decreased until the cage curtain can be opened slightly without a noticeable change in signal (room lights should be out, of course). Then, while imaging, the PMT positions can be changed by hand while observing the signal. The signal should be seen to have a maximum within reach of both x and y adjustments. It should be possible to adjust x and y separately, and set the screw tension on the adjustment plates such that a position will be held when one’s hand is removed. Then the screws can be tightened to lock down the position.

## c) Resonant mirror edge blocks

The two independent beam blocks right after the Special Optics scan lens are for blocking the edges of the resonant mirror scan pattern, so that unnecessary light is not applied to the sample as the resonant mirror turns around. These are adjusted manually.

# 5) Regular alignment procedure

This alignment procedure should be performed regularly (e.g. daily) to ensure that there has not been beam wander, unless it has been observed that regular adjustment is not necessary.

            1. Remove objective and attach alignment jig in its place. In the 3d model, both objective and alignment jig are shown attached at the same time, overlapping one another.
            2. Open the upper iris in the alignment jig wide. Observe the beam passing through this iris with a beam viewing screen (paper or Thorlabs VRC4). Adjust the “main table optics alignment mirror” (see section 4)a)7 ) to center the beam in the iris. This adjusts the beam centration at the objective.
            3. Adjust the lower iris in the alignment jig to a diameter of approx. 2-3mm. Adjust the upper iris until it is slightly larger than this, such that a shadow of the upper iris in the beam forms a thin ring around the lower iris. If this shadow is not centered with the lower iris, then it can be adjusted either by adjusting the galvo mirror angle, res mirror angle, or the mirror right before the resonant mirror. This adjusts the beam angle at the objective (centering the scan field on the objective field).
            4. Repeat steps 2 and 3 iteratively, adjusting as necessary, until beam position and angle at objective are both satisfactory. In the future, it will usually be sufficient to only perform step 2.

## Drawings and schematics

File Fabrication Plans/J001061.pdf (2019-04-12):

# VIEW M-M

# SECTION N-N

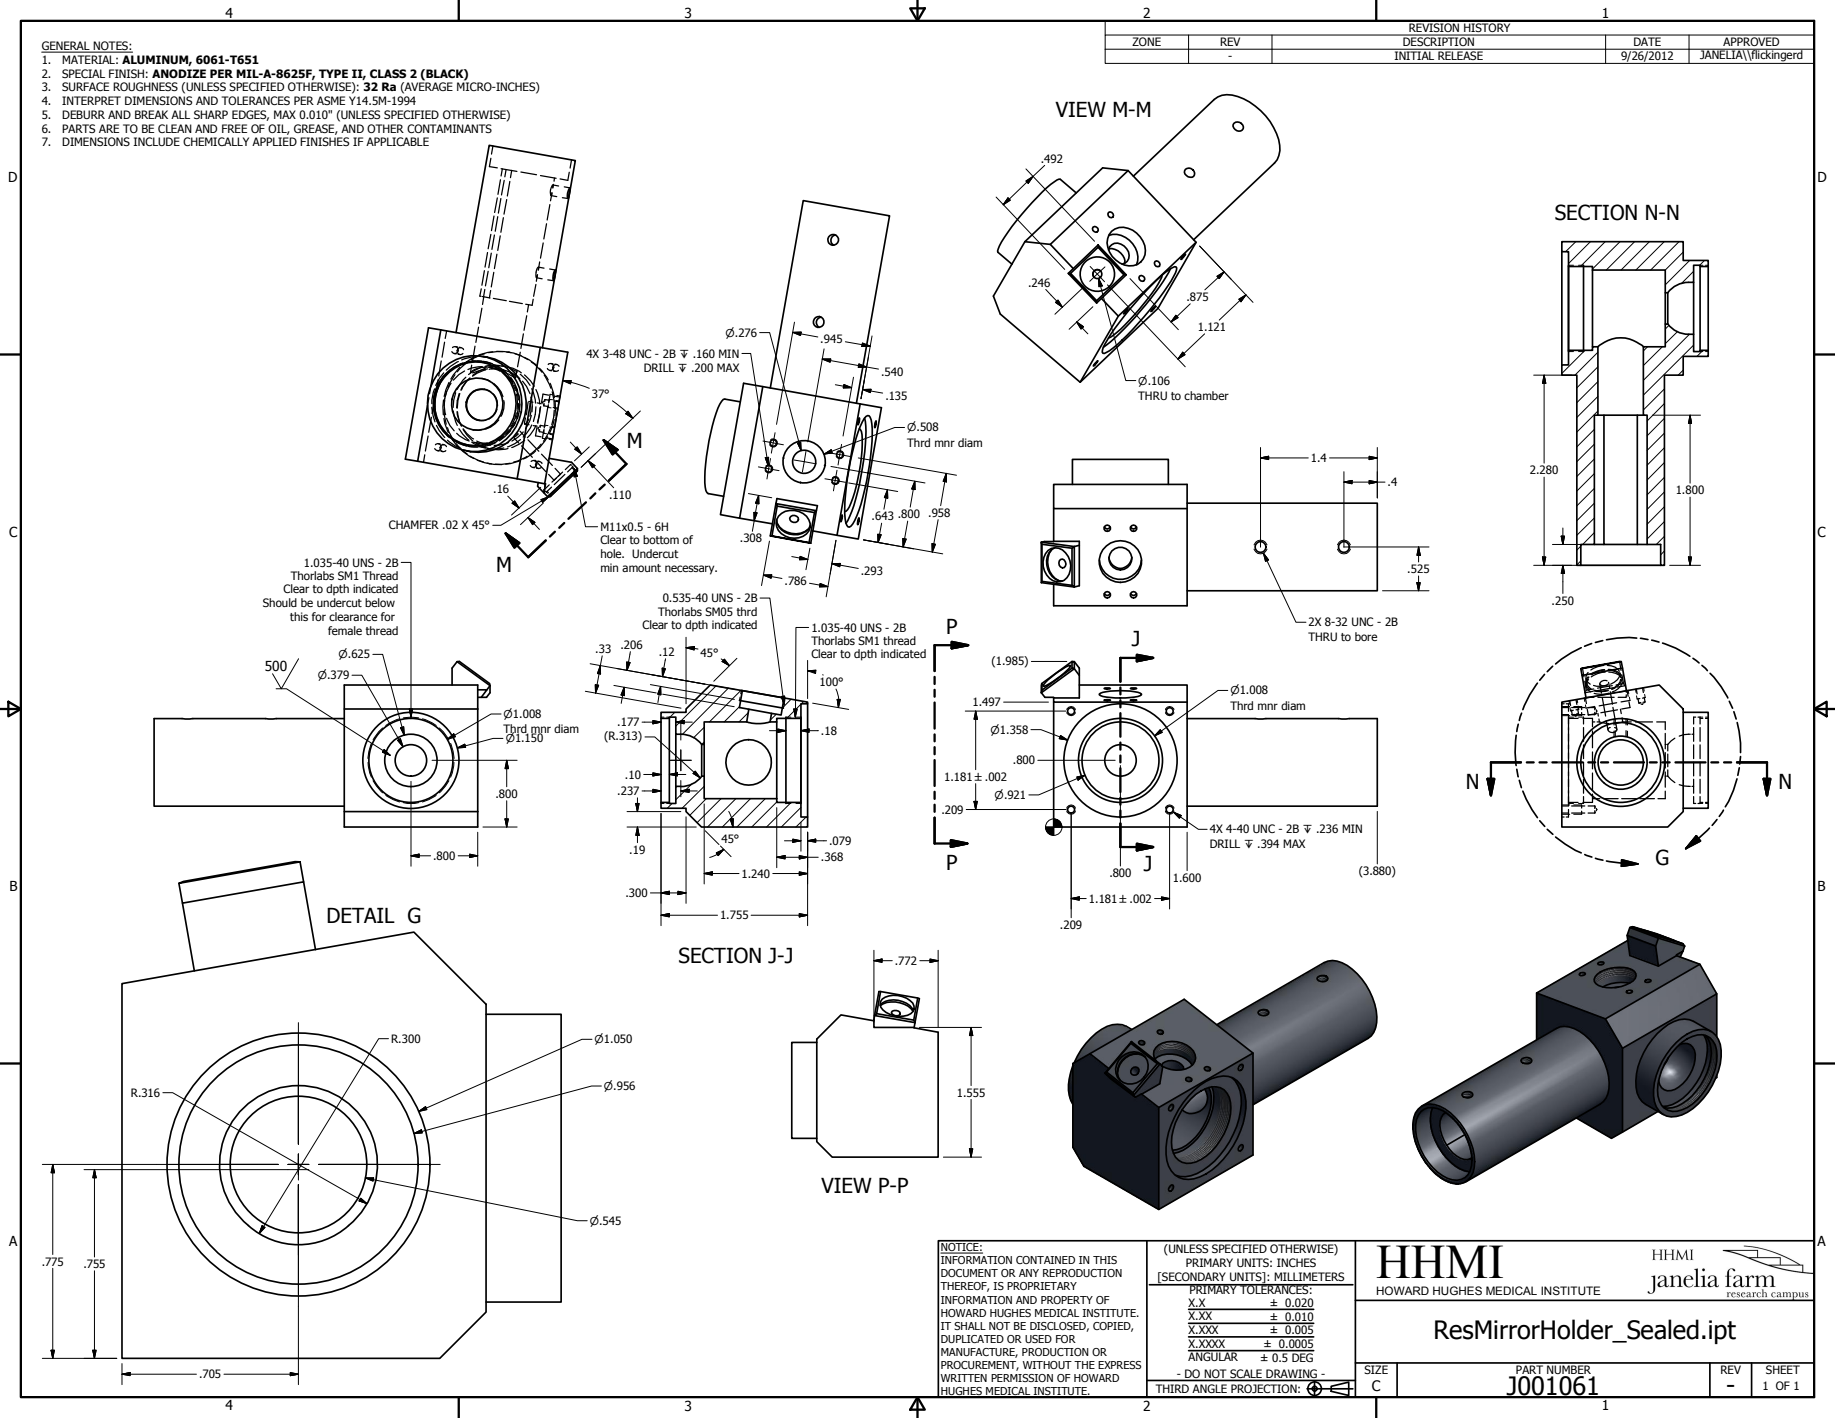
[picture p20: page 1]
DETAIL G; SECTION J-J; VIEW P-P; PART NUMBER; HHMI; SIZE; REV; SHEET; 1 OF 1 THIRD ANGLE PROJECTION:; ± 0.020 ± 0.010 ± 0.005 ± 0.0005 ± 0.5 DEG; REVISION HISTORY; ZONE; DESCRIPTION; DATE; APPROVED; INITIAL RELEASE; JANELIA\\flickingerd; 4X 4-40 UNC - 2B Z .236 MIN DRILL Z .394 MAX; 4X 3-48 UNC - 2B Z .160 MIN DRILL Z .200 MAX; 0.535-40 UNS - 2B Thorlabs SM05 thrd Clear to dpth indicated; Thrd mnr diam; female thread; CHAMFER .02 X 45°

GENERAL NOTES:
1. MATERIAL: ALUMINUM, 6061-T651
2. SPECIAL FINISH: ANODIZE PER MIL-A-8625F, TYPE II, CLASS 2 (BLACK)
3. SURFACE ROUGHNESS (UNLESS SPECIFIED OTHERWISE): 32 Ra (AVERAGE MICRO-INCHES)
4. INTERPRET DIMENSIONS AND TOLERANCES PER ASME Y14.5M-1994
5. DEBURR AND BREAK ALL SHARP EDGES, MAX 0.010" (UNLESS SPECIFIED OTHERWISE)
6. PARTS ARE TO BE CLEAN AND FREE OF OIL, GREASE, AND OTHER CONTAMINANTS
7. DIMENSIONS INCLUDE CHEMICALLY APPLIED FINISHES IF APPLICABLE

THRU to chamber

Thrd mnr diam

Clear to bottom of
hole. Undercut
min amount necessary.

1.035-40 UNS - 2B
Thorlabs SM1 Thread
Clear to dpth indicated
Should be undercut below
this for clearance for

Thorlabs SM1 thread

2X 8-32 UNC - 2B
THRU to bore

NOTICE:
INFORMATION CONTAINED IN THIS
DOCUMENT OR ANY REPRODUCTION
THEREOF, IS PROPRIETARY
INFORMATION AND PROPERTY OF
HOWARD HUGHES MEDICAL INSTITUTE.
IT SHALL NOT BE DISCLOSED, COPIED,
DUPLICATED OR USED FOR
MANUFACTURE, PRODUCTION OR
PROCUREMENT, WITHOUT THE EXPRESS
WRITTEN PERMISSION OF HOWARD
HUGHES MEDICAL INSTITUTE.

(UNLESS SPECIFIED OTHERWISE)
PRIMARY UNITS: INCHES
[SECONDARY UNITS]: MILLIMETERS
PRIMARY TOLERANCES:
X.XXX
X.XXXX
ANGULAR
- DO NOT SCALE DRAWING -

HOWARD HUGHES MEDICAL INSTITUTE
ResMirrorHolder_Sealed.ipt

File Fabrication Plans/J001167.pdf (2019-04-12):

D

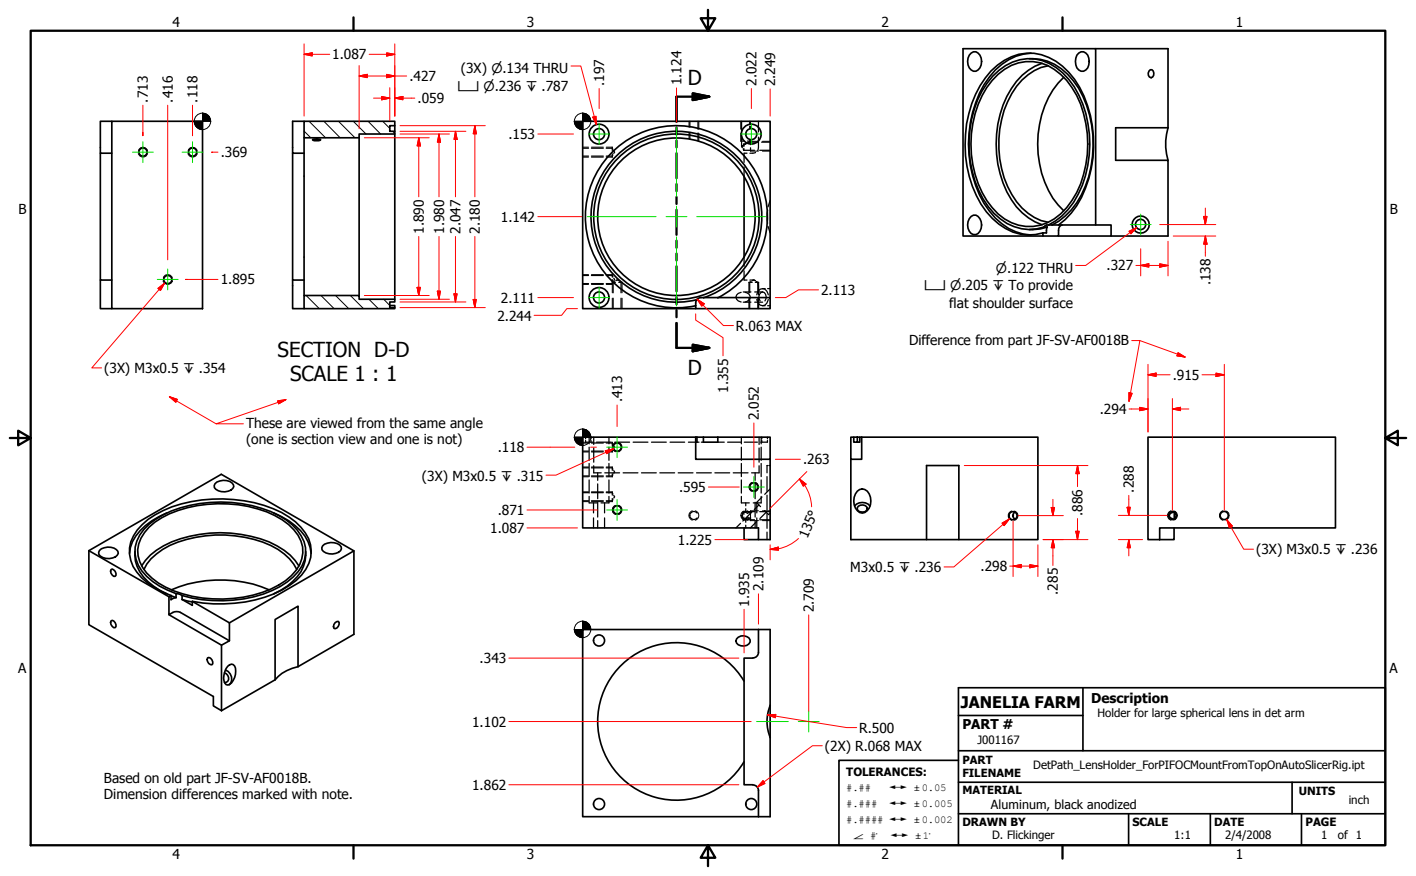
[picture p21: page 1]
SECTION D-D; SCALE 1 : 1; JANELIA FARM; PART #; PART FILENAME; MATERIAL; DRAWN BY; SCALE; DATE; DetPath_LensHolder_ForPIFOCMountFromTopOnAutoSlicerRig.ipt; Aluminum, black anodized; UNITS; D. Flickinger; PAGE; inch; TOLERANCES:; R.063 MAX; (3X) P.134 THRU X P.236 Z .787; P.122 THRU; (2X) R.068 MAX

X P.205 Z To provide
flat shoulder surface

Difference from part JF-SV-AF0018B

These are viewed from the same angle
(one is section view and one is not)

Description
Holder for large spherical lens in det arm

Based on old part JF-SV-AF0018B.
Dimension differences marked with note.

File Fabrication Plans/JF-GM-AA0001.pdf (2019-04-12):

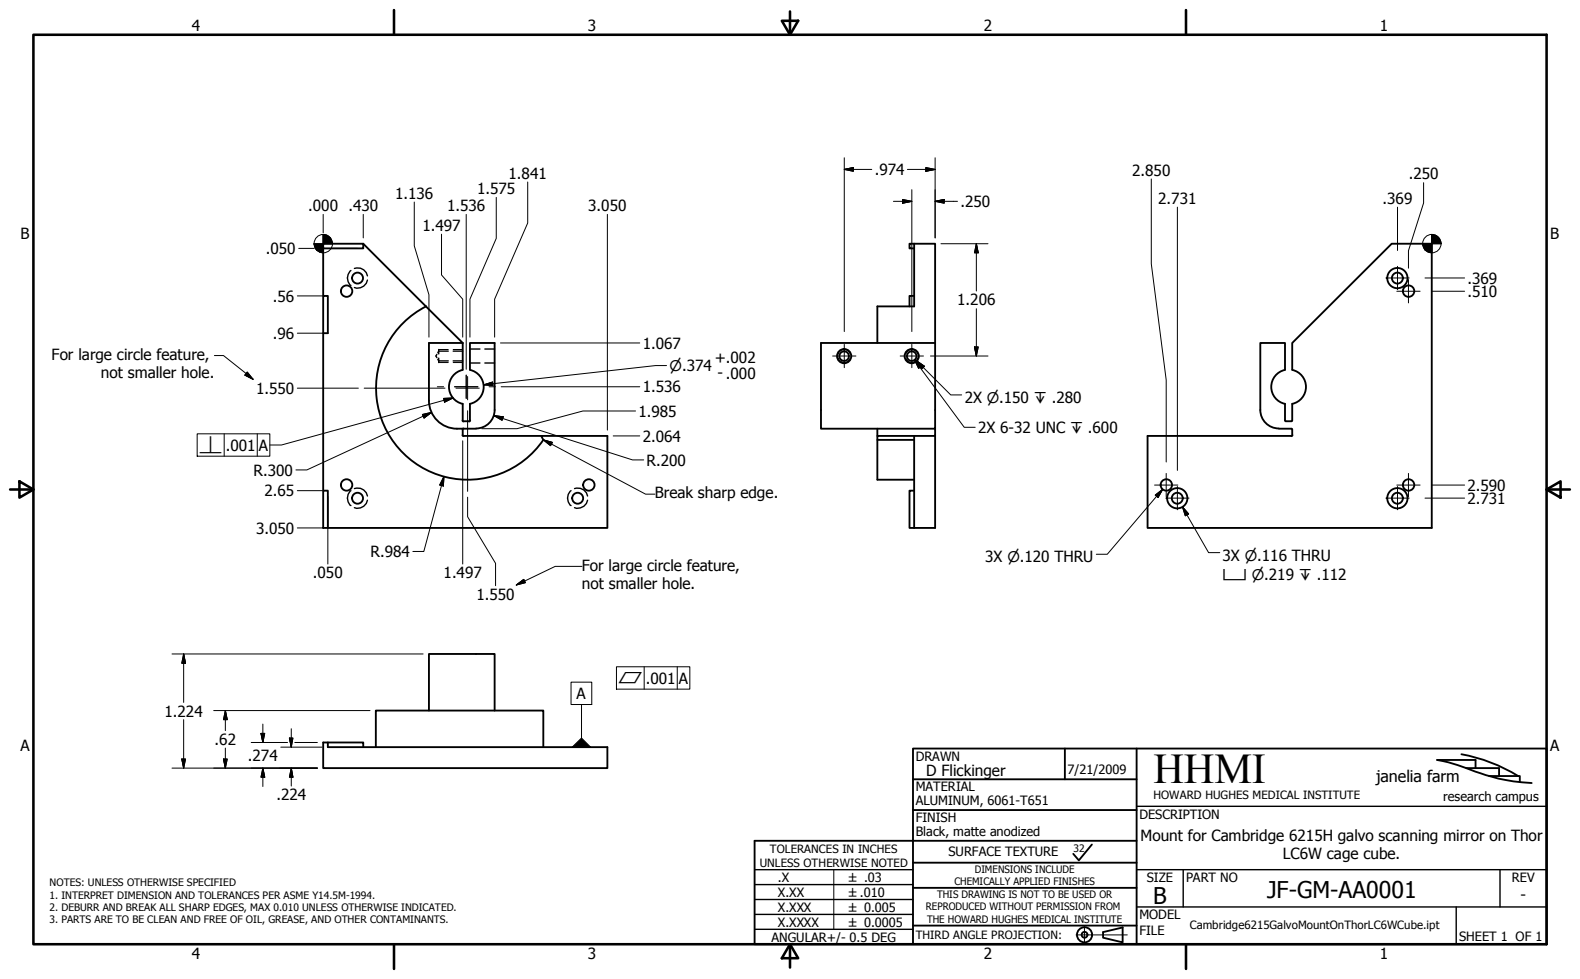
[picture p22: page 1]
SHEET 1 OF 1; DRAWN; PART NO; LC6W cage cube.; SIZE B; REV -; FINISH; MATERIAL; SURFACE TEXTURE; HHMI; janelia farm; research campus; MODEL FILE; Cambridge6215GalvoMountOnThorLC6WCube.ipt; ALUMINUM, 6061-T651; Black, matte anodized; X.XXXX; 2X 6-32 UNC Z .600; 3X P.116 THRU X P.219 Z .112; 3X P.120 THRU; D Flickinger

For large circle feature,

not smaller hole.

Break sharp edge.

HOWARD HUGHES MEDICAL INSTITUTE
DESCRIPTION
Mount for Cambridge 6215H galvo scanning mirror on Thor

TOLERANCES IN INCHES
UNLESS OTHERWISE NOTED
X.XXX
ANGULAR+/- 0.5 DEG

DIMENSIONS INCLUDE
CHEMICALLY APPLIED FINISHES
THIS DRAWING IS NOT TO BE USED OR
REPRODUCED WITHOUT PERMISSION FROM
THE HOWARD HUGHES MEDICAL INSTITUTE
THIRD ANGLE PROJECTION:

NOTES: UNLESS OTHERWISE SPECIFIED
1. INTERPRET DIMENSION AND TOLERANCES PER ASME Y14.5M-1994.
2. DEBURR AND BREAK ALL SHARP EDGES, MAX 0.010 UNLESS OTHERWISE INDICATED.
3. PARTS ARE TO BE CLEAN AND FREE OF OIL, GREASE, AND OTHER CONTAMINANTS.

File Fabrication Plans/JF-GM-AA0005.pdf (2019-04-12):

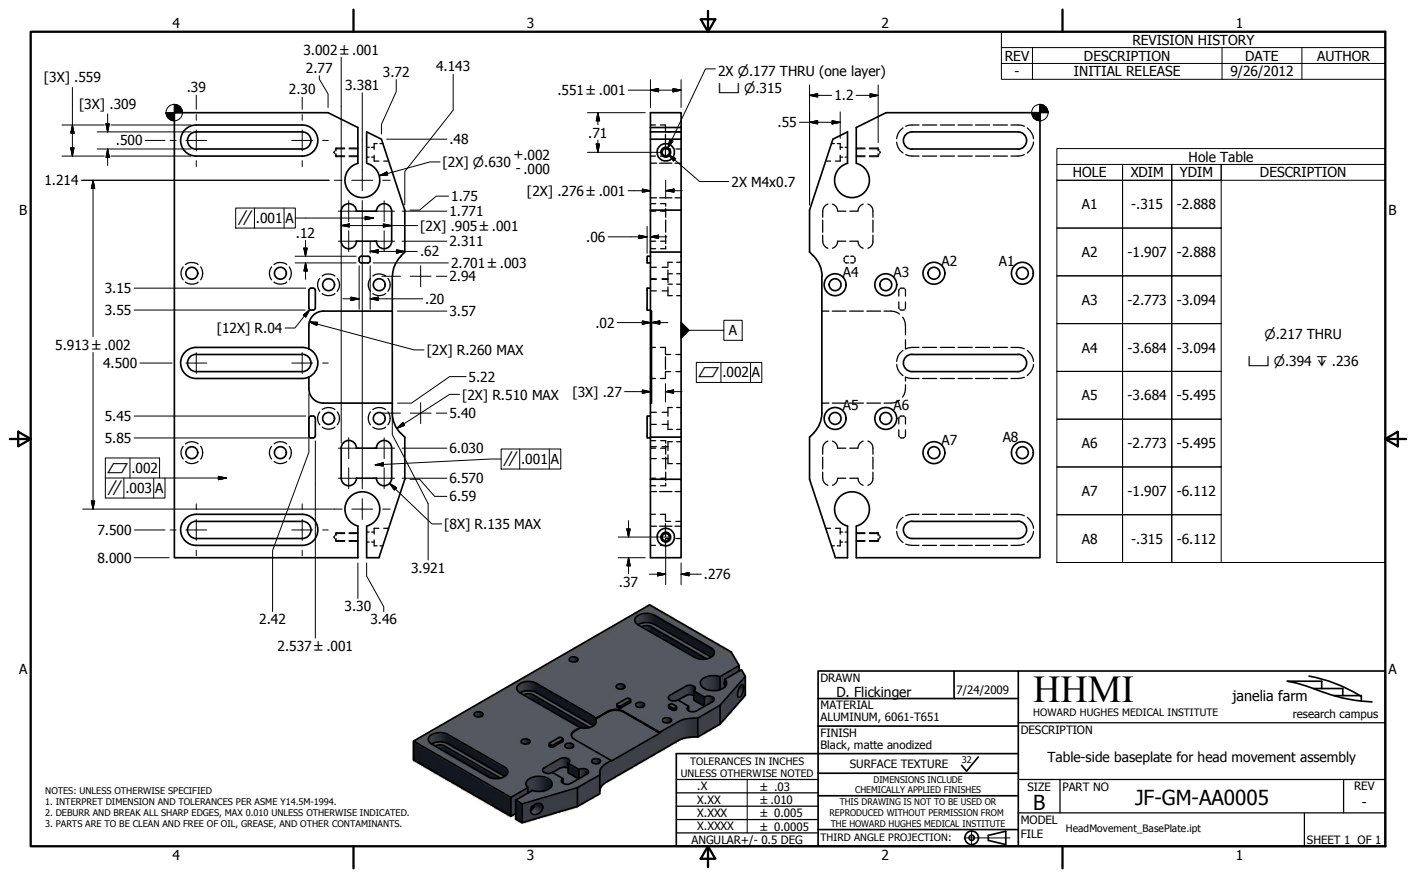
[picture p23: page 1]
SHEET 1 OF 1; DRAWN; PART NO; SIZE B; REV -; FINISH; MATERIAL; SURFACE TEXTURE; HHMI; janelia farm; research campus; MODEL FILE; HeadMovement_BasePlate.ipt; ALUMINUM, 6061-T651; Black, matte anodized; X.XXXX; REVISION HISTORY; REV; DESCRIPTION; DATE; AUTHOR; INITIAL RELEASE; [8X] R.135 MAX; [2X] R.260 MAX; [2X] R.510 MAX; Hole Table; HOLE; XDIM; YDIM; P.217 THRU; D. Flickinger

2X P.177 THRU (one layer)

HOWARD HUGHES MEDICAL INSTITUTE
DESCRIPTION

Table-side baseplate for head movement assembly

TOLERANCES IN INCHES
UNLESS OTHERWISE NOTED
X.XXX
ANGULAR+/- 0.5 DEG

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

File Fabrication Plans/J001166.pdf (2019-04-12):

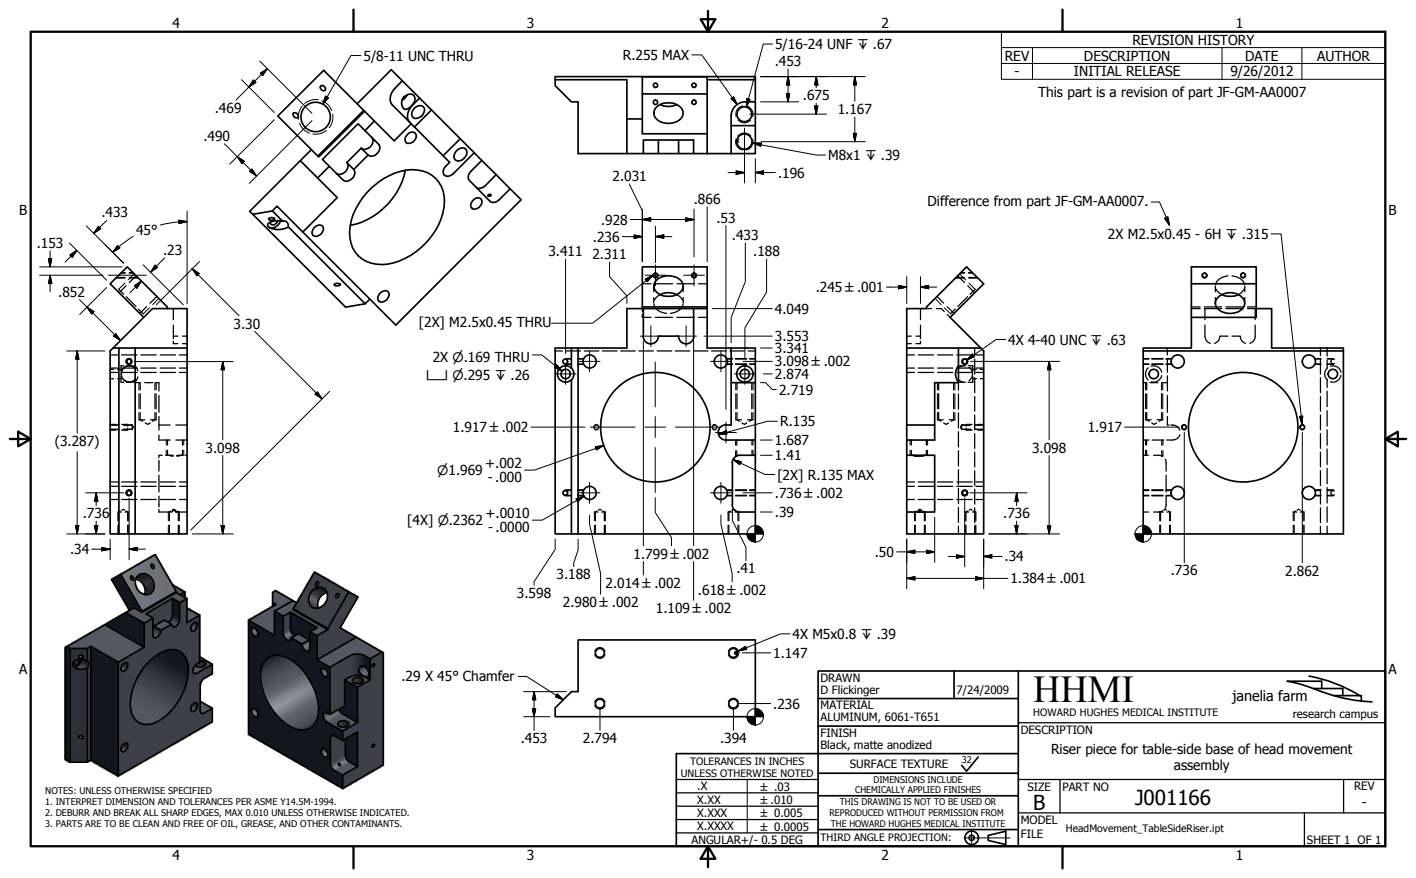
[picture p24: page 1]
SHEET 1 OF 1; D Flickinger; PART NO; assembly; SIZE B; REV -; HHMI; janelia farm; research campus; MODEL FILE; HeadMovement_TableSideRiser.ipt; X.XXXX; REVISION HISTORY; REV; DESCRIPTION; DATE; AUTHOR; INITIAL RELEASE; [2X] R.135 MAX; 2X P.169 THRU X P.295 Z .26; [2X] M2.5x0.45 THRU; .29 X 45° Chamfer; 4X 4-40 UNC Z .63; 5/8-11 UNC THRU; R.255 MAX; 5/16-24 UNF Z .67

This part is a revision of part JF-GM-AA0007

Difference from part JF-GM-AA0007.

DRAWN
MATERIAL
ALUMINUM, 6061-T651
FINISH
Black, matte anodized
SURFACE TEXTURE

HOWARD HUGHES MEDICAL INSTITUTE
DESCRIPTION
Riser piece for table-side base of head movement

TOLERANCES IN INCHES
UNLESS OTHERWISE NOTED
X.XXX
ANGULAR+/- 0.5 DEG

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

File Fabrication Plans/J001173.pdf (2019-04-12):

# SECTION A-A

D

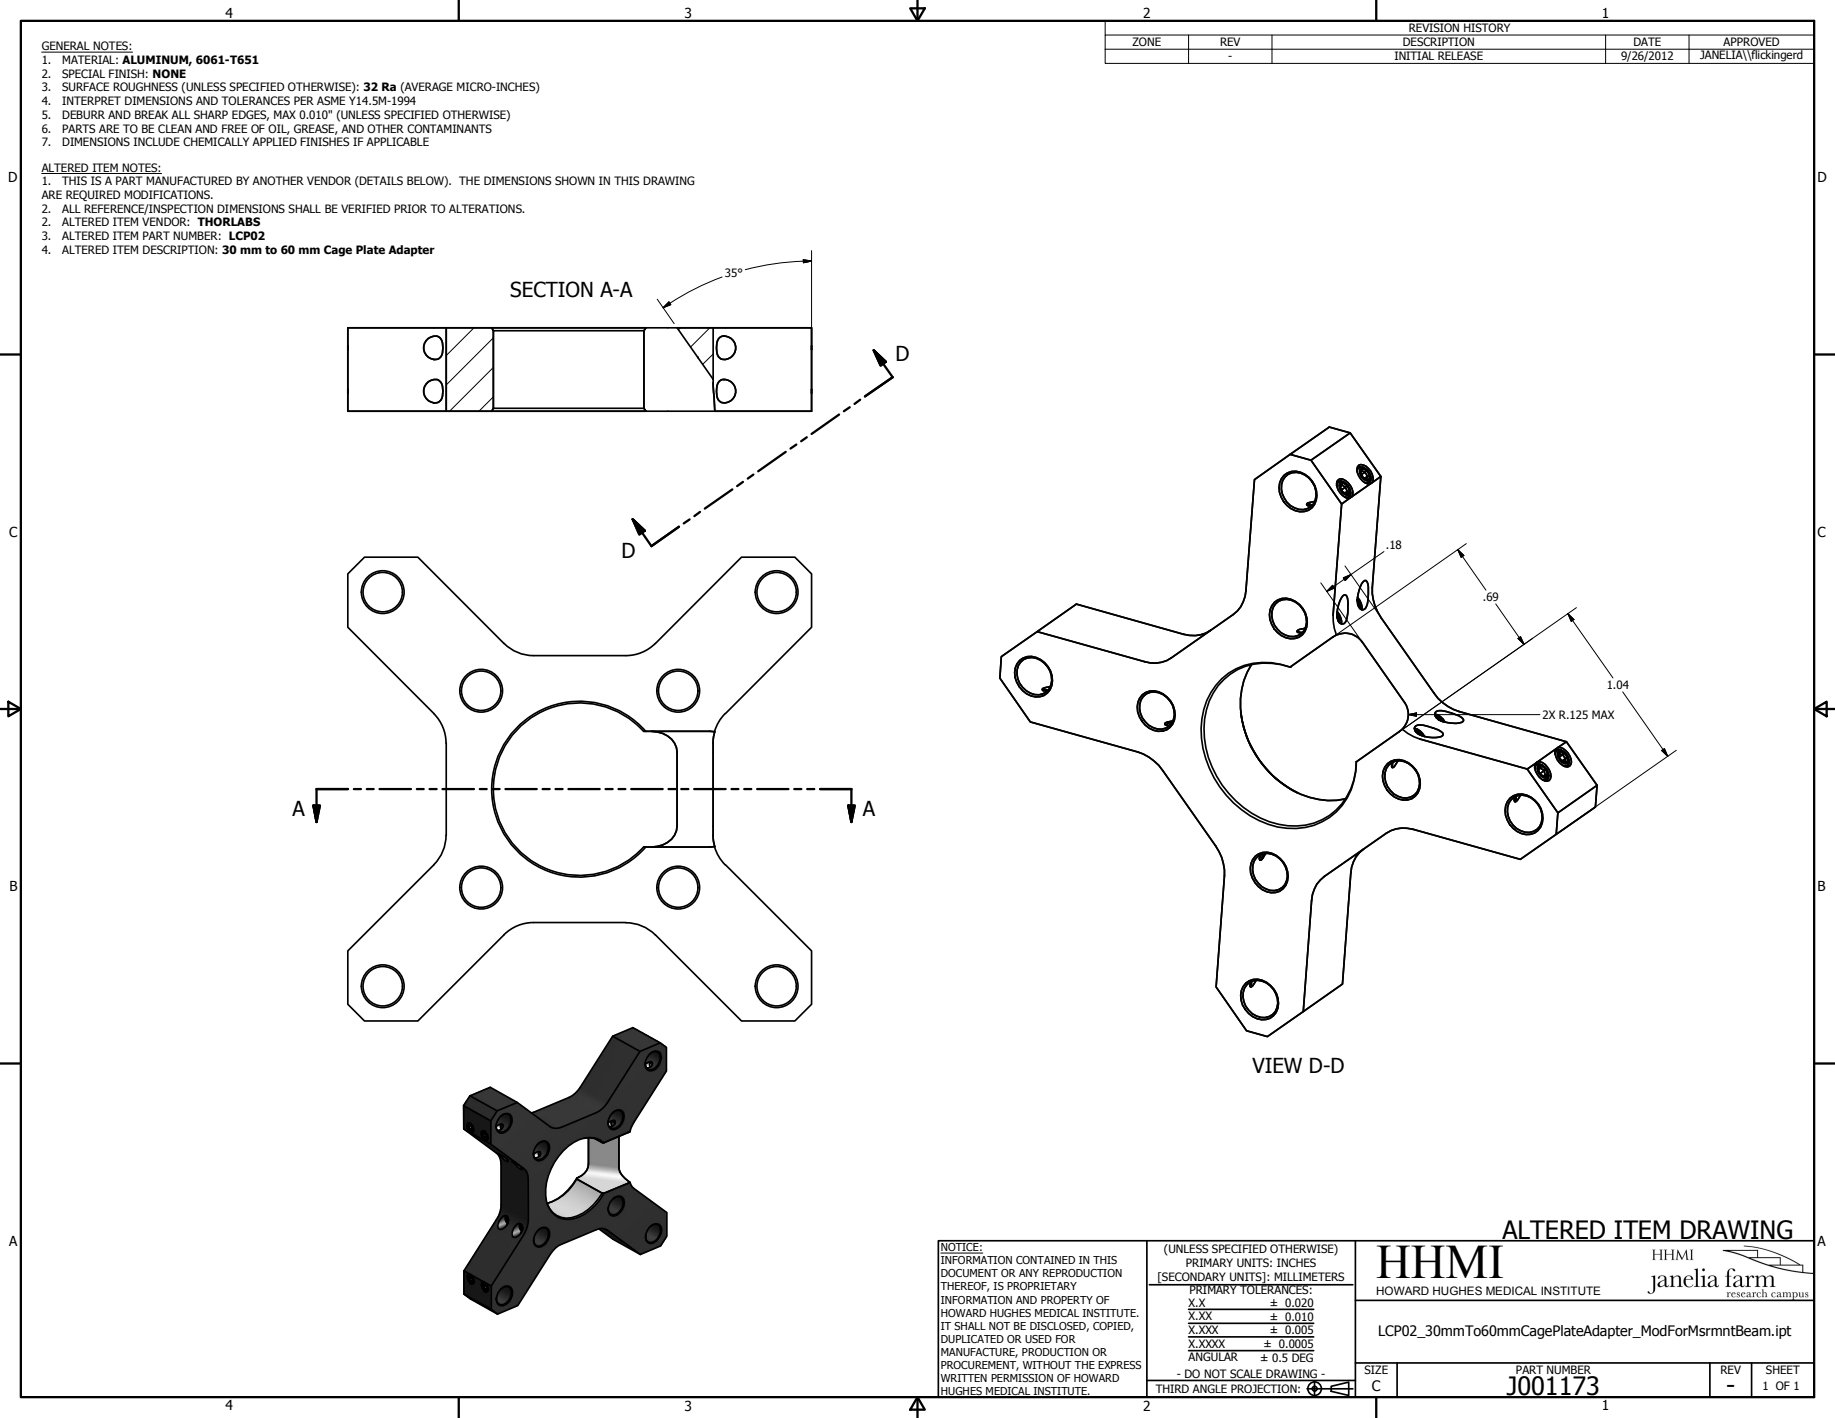
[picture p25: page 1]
VIEW D-D; PART NUMBER; SIZE; REV; SHEET; 1 OF 1 THIRD ANGLE PROJECTION:; ± 0.020 ± 0.010 ± 0.005 ± 0.0005 ± 0.5 DEG; LCP02_30mmTo60mmCagePlateAdapter_ModForMsrmntBeam.ipt; REVISION HISTORY; ZONE; DESCRIPTION; DATE; APPROVED; INITIAL RELEASE; JANELIA\\flickingerd; 2X R.125 MAX

GENERAL NOTES:
1. MATERIAL: ALUMINUM, 6061-T651
2. SPECIAL FINISH: NONE
3. SURFACE ROUGHNESS (UNLESS SPECIFIED OTHERWISE): 32 Ra (AVERAGE MICRO-INCHES)
4. INTERPRET DIMENSIONS AND TOLERANCES PER ASME Y14.5M-1994
5. DEBURR AND BREAK ALL SHARP EDGES, MAX 0.010" (UNLESS SPECIFIED OTHERWISE)
6. PARTS ARE TO BE CLEAN AND FREE OF OIL, GREASE, AND OTHER CONTAMINANTS
7. DIMENSIONS INCLUDE CHEMICALLY APPLIED FINISHES IF APPLICABLE

ALTERED ITEM NOTES:

1. THIS IS A PART MANUFACTURED BY ANOTHER VENDOR (DETAILS BELOW). THE DIMENSIONS SHOWN IN THIS DRAWING
ARE REQUIRED MODIFICATIONS.
2. ALL REFERENCE/INSPECTION DIMENSIONS SHALL BE VERIFIED PRIOR TO ALTERATIONS.
2. ALTERED ITEM VENDOR: THORLABS
3. ALTERED ITEM PART NUMBER: LCP02
4. ALTERED ITEM DESCRIPTION: 30 mm to 60 mm Cage Plate Adapter

ALTERED ITEM DRAWING
HHMI

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

HOWARD HUGHES MEDICAL INSTITUTE

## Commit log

2019-04-12 Reorganized and updated
    [Galvo Driver Heatsink.dwg, GalvoDriver_BOM.xlsx, Heatsink.ipt, J001179_hard_inch.stl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]
2019-04-12 renamed some files
    [MouseLight_Microscope_PartsList.xlsx]
2019-04-12 Updated assembly guide
